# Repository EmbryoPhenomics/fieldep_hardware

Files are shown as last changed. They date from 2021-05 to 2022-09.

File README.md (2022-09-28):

# fieldep_hardware
CAD files and build guides for FieldEP hardware.

Latest version of hardware comprises a camera module and a light module.

**Camera module:**
* [RPi 4](https://thepihut.com/products/raspberry-pi-4-model-b?variant=31994565689406&currency=GBP&utm_medium=product_sync&utm_source=google&utm_content=sag_organic&utm_campaign=sag_organic&gclid=Cj0KCQjwqp-LBhDQARIsAO0a6aJ3-eRsvUKjcBT1Sl6JbVKJ5IVJRQNQ4zsPwrIjGK0_9DRzZ2UdX3kaAvDAEALw_wcB)
* [Ablelectronics Breakout Pi Zero](https://www.abelectronics.co.uk/p/68/breakout-pi-zero)
* [PiJuice Zero](https://uk.pi-supply.com/products/pijuice-zero)
* [Waveshare Sim7000E](https://www.unmannedtechshop.co.uk/product/nb-iot-emtc-edge-gprs-gnss-hat-for-raspberry-pi/)
* 3.7V [12000 mAh Lithium battery](https://uk.pi-supply.com/products/pijuice-12000mah-battery)

**Light module:**
* [Sparkfun Lumidrive](https://coolcomponents.co.uk/products/lumidrive-led-driver)
* [Lumini 2" LED ring](https://coolcomponents.co.uk/products/lumini-led-ring-2-inch-40-x-apa102-2020?_pos=3&_sid=d6814a536&_ss=r)
* 3.7V Battery as big as possible. Something like [this](https://uk.pi-supply.com/products/lithium-ion-battery-pack-3-7v-4400mah) as a minimum.

<iframe src="https://myhub.autodesk360.com/ue2c78370/shares/public/SH9285eQTcf875d3c539a6b3ce2d492fae0a?mode=embed" width="640" height="480" allowfullscreen="true" webkitallowfullscreen="true" mozallowfullscreen="true"  frameborder="0"></iframe>

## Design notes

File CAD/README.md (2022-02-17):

This folder contains STL files for FieldEP electronics supports, frame and stage. 

## Internal components

Tray_plate_3-inch_Mk3_2022-Feb-17_03-37-20PM-000_CustomizedView10696725587

|Part|Note|
|----|----|
|Front plate|Fixes to O-ring flange using 4x M3x8mm countersunk precision screws|
|Rear plate|Fixes to O-ring flange using 2x M3x8mm countersunk, and 2x M3x8mm cap head precision screws|
|Offset tray|Bolts to rear plate using 1x M3x6mm cap head precision screw. Forward end of tray supported by slots in front plate|
|Tray supports|One pair, fixed to rear end of Offset tray using 2x M3x8mm countersunk precision screws per support|
|Lens mounting brackets|Minimum of one pair required. Two pairs recommended. Specific to this [microscope lens](https://shop.pimoroni.com/products/microscope-lens-0-12-1-8x); Bolted through tray using M3x14mm precision screws, hex nuts and washers between lower lens bracket and tray as required|
|Hardware summary|
|M3 X 8mm countersunk|x10|
|M3 x 8mm cap head|x3|
|M3 x 14mm cap head|x4|
|M3 hex nut|x4|
|M3 washer|x8|

Tray_plate_3-inch_Mk3_2022-Feb-17_02-23-52PM-000_CustomizedView29439711389

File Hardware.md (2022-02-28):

# Hardware configuration

## Housing

FieldEP comprises two submersible housings - cylinders of 76.2 mm internal diameter with aluminium flanges and an acrylic front window. Electronic hardware and a microscope lens are supported within the housing by a 3D-printed structure consisting of a front plate, rear plate and a tray. A LiPo battery is held underneath the tray to provide primary power to the electronics. 

The second housing is used as an auxiliary battery chamber and LED lamp which illuminates subjects from the rear, towards the camera. Animals of interest are held between the two housings on an adjustable stage, held in place with nuts on threaded bar.
99fb7549-5d30-4ef4-b056-59008e5c76de

The modular design of the support structures inside the housing allows for ease of printing on non-specialist 3D printers, and accommodates changes to electronics and battery space requirements via minor changes to the lens supports which are bolted to the forward protrusions of the electronics tray.

To summarise the main components and their function, the Raspberry Pi takes and records inputs (sensors, cameras), and transmits to a cloud-based dashboard. Power management and timing is handled by a Pi Supply PiJuice Zero, which also takes a user input to initiate bootup. Power is supplied by a LiPo cell for powering the Pi, and a D-cell battery pack which keeps the LiPo cell charged via the PiJuice Zero, and powers the LED light.

FieldEP diagram v2 drawio(1)

## Electronic components
Stacking headers are used to connect the main components to the Raspberry Pi. Stacking moPiJuicedules are connected in the order:
|Pi HAT|
|---|
|GSM Module|
|PiJuice|
|PiZero Breakout|
|Raspberry Pi Zero W 2|

Pin headers are also broken out to allow for connection to other modules. For the operation of sensors and communications the connections are broken out to a 90-degree pin header for connection via jumper wires.

|1|2|3|4|5|6|7|8|9|10|11|12|13|14|15|16|17|18|19|20|
|---|---|---|---|---|---|---|---|---|---|---|---|---|---|---|---|---|---|---|---|
|  |TX|RX| |  |  |  |  |  |  |  |  |GPIO25|GND|  |  |  |GPIO26|GND|  |
|21|22|23|24|25|26|27|28|29|30|31|32|33|34|35|36|37|38|39|40|
|3.3V|SCL|SDA|GND|  |  |  |  |  |  |  |  |  |  |  |  |  |  |  |  |  |

## Housing parts list:
* Blue Robotics 3" housing
    - [298mm Acrylic tube](https://bluerobotics.com/store/watertight-enclosures/3-series/wte3-p-tube-12-r1/) (x2)
    - [O-ring flange](https://bluerobotics.com/store/watertight-enclosures/3-series/o-ring-flange-3-series/) (x4)
    - [Aluminium end cap - 7-hole](https://bluerobotics.com/store/watertight-enclosures/3-series/wte3-m-end-cap-7-hole-r1/)
    - [Aluminium end cap - 4-hole](https://bluerobotics.com/store/watertight-enclosures/3-series/wte3-m-end-cap-4-hole-r1/)
    - [Acrylic end cap](https://bluerobotics.com/store/watertight-enclosures/3-series/wte3-p-end-cap-r1/) (x2)
    - [Switch](https://bluerobotics.com/store/comm-control-power/switch/switch-10-5a-r1/) (x2)
    - [M10 vent & plug](https://bluerobotics.com/store/cables-connectors/penetrators/vent-asm-r1/)
    - M10 penetrator for 3mm cable
    - M10 penetrator for 4.5 mm cable
    - M3 x 16 mm screws (x 20 - included with end caps)
* M8 x 250 mm threaded bar (x4)
* Faceplate
* Rear plate
* Electronics tray
* [M3 x 10 mm cap head screws](https://www.accu.co.uk/en/cap-head-screws/3975-SSCF-M3-10-A4) (x 12)
* [M3 x 16 mm cap head screws](https://www.accu.co.uk/en/cap-head-screws/3978-SSCF-M3-16-A4) (x 4)
* [M3 x 8 mm cap head screws](https://www.accu.co.uk/en/cap-head-screws/3974-SSCF-M3-8-A4) (x 3)
* [M3 x 8 mm countersunk screws](https://www.accu.co.uk/en/countersunk-socket-head-screws/5596-SSK-M3-8-A4) (x 10)
* _[M2.5 x 10 cap head screws](https://www.accu.co.uk/en/cap-head-screws/3964-SSCF-M2-5-10-A4) (x 4)_

## Electronic components
**Camera module:**
* [Raspberry Pi Zero 2 W](https://thepihut.com/products/raspberry-pi-zero-2)
* Arducam HQ camera module
* [PiJuice Zero](https://uk.pi-supply.com/products/pijuice-zero)
* [Waveshare GSM7000e SIM module](https://www.unmannedtechshop.co.uk/product/nb-iot-emtc-edge-gprs-gnss-hat-for-raspberry-pi/)
* GSM Antenna
* SIM card
* SMA connector
* Blue Robotics TSYS01 temperature sensor
* Blue Robotics I2C bus splitter
* [3.7V 12000 mAh Lithium cell](https://uk.pi-supply.com/products/pijuice-12000mah-battery)
* [Ablelectronics Breakout PiZero](https://www.abelectronics.co.uk/p/68/breakout-pi-zero)
* Extra long stacking pin header for Raspberry Pi (15 mm pins)

**Light module:**
* [Sparkfun Lumidrive](https://coolcomponents.co.uk/products/lumidrive-led-driver)
* [Lumini 2" LED ring](https://coolcomponents.co.uk/products/lumini-led-ring-2-inch-40-x-apa102-2020?_pos=3&_sid=d6814a536&_ss=r)
* 3.7V Battery as big as possible. Something like [this](https://uk.pi-supply.com/products/lithium-ion-battery-pack-3-7v-4400mah) as a minimum.

_To be developed when time allows: Transistor-based switching of LED module to enable full power-down when not required. Suggested approach:_

## LED circuit

The LED light comprises an array of WS2812 LEDs, controlled via the Raspberry Pi and powered using an external battery. The LED circuit is switched using an N-channel MOSFET. 

|Schematic|Breadboard|
|----------|---------|
|LED MOSFET FieldEP_schem|LED MOSFET FieldEP_bb v2|

|Part|Detail|Role|Note|
|-----|-----|-----|-----|
|R1|330 &Omega; |Protect Pi GPIO from overcurrent| Calculated: _R = V/I_ where V is the power supply voltage (4.8V) and I is the max GPIO current for Pi GPIO (16 mA)|
|R2|100 k&Omega;|Pull-down resistor|Ensure Gate pin on MOSFET is stable|Recommend high value|
|Q1|[IRLB8721](https://uk.rs-online.com/web/p/mosfets/7259322)|Switches LED circuit|Logic-level N-channel MOSFET. Relies on voltage difference between Gate and Source (Pins 1 & 3). Alternatives include [IRLZ44ZPBF](https://uk.rs-online.com/web/p/mosfets/6887308) and [FQP30N06L](https://uk.rs-online.com/web/p/mosfets/8075863)|
|WS2812|RGB LED|Illumination!|May need a 1N4001 diode between battery positive terminal and VDD if unexpected behaviour occurs due to logic level discrepancy between Pi (3.3V) and LED (5V)| 
|C1|1000 &mu;F|Compensates for spikes in current draw|Recommended but not essential|

https://bluerobotics.com/store/cables-connectors/penetrators/penetrator-10-25-a/
https://bluerobotics.com/store/cables-connectors/penetrators/penetrator-blank-10-25-a-r2/

## Consumables
* Solder
* [Epoxy encapsulant] (https://uk.rs-online.com/web/p/potting-compounds/1991430/?cm_mmc=UK-PLA-DS3A-_-google-_-CSS_UK_EN_Adhesives_%26_Sealants_%26_Tapes_Whoop-_-Potting+Compounds_Whoop+(2)-_-1991430&matchtype=&pla-361646333034&gclid=Cj0KCQiA-aGCBhCwARIsAHDl5x_ZlQvM5ZzL2Q7NVCp0c83qOvFK9o2Kul7I_UrpGSP3q1dLpcyBrxwaAjktEALw_wcB&gclsrc=aw.ds)
* Wire (22 AWG)

## Switch mode operation
FieldEP is designed to boot up into one of two modes. The process of bootup up is the same regardless of which mode is required. The _Boot_ switch is momentarily partially unscrewed (3(?) full turns). This initiates a boot cycle, whereby the state of the _Mode_ switch is monitored, and the system boots into the selected mode. 

During Live View mode, a change in state of the _Mode_ switch will power the system down. 

A typical deployment procedure would be:

1) Position stage approximately where laboratory testing has shown focus point to be with chosen magnification
2) Set _Mode_ to _Live_
3) Boot system by momentarily unscrewing _Boot_ switch until system powers up
4) Close _Boot_ switch
5) Immerse system in shallow water, LED lamp module first
6) Monitor live view whilst manipulating position of stage until focus is achieved
7) Change _mode_ switch to _Deployment_ by fully screwing closed
8) Boot system by momentarily unscrewing _Boot_ switch until system powers up

Step 8 initiates an acquisition cycle. The first acquisition will occur immediately and subsequent acquisitions will occur according to the time delay set in config.json.

Operation modes - coloured background

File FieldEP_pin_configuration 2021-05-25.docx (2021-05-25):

Function | Module | GPIO | Pin # | | GPIO | Module | Function
Sensor power | I2C sensors | 3.3V | 1 | 2 | 5V
Sensor SDA | I2C sensors | GPIO2 SDA (I²C) | 3 | 4 | 5V
Sensor SCK | I2C sensors | GPIO3 SCK (I²C) | 5 | 6 | GND | I2C sensor GND | GND
| | GPIO4 | 7 | 8 | GPIO14 (UART TX) | SIM800 RX | Receive
| | GND | 9 | 10 | GPIO15 (UART RX) | SIM800 TX | Transmit
| | GPIO17 Chip Enable-CE1 (SPI1) | 11 | 12 | GPIO18 Chip Enable-CE0 (SPI1) [PWM] | LiPo Shim Pin 12 | Low-voltage shutdown signal
| | GPIO27 | 13 | 14 | GND | SIM800 GND | GND
| | GPIO22 | 15 | 16 | GPIO23
3.3V ref voltage | LiPo Shim | 3.3V | 17 | 18 | GPIO24
| | GPIO10 MOSI (SPI0) | 19 | 20 | GND
| | GPIO9 MISO (SPI0) | 21 | 22 | GPIO25
| | GPIO SCLK (SPI0) | 23 | 24 | GPIO8 Chip Enable-CE0 (SPI0)
| | GND | 25 | 26 | GPIO7 Chip Enable-CE1 (SPI0)
| | GPIO 0 EEPROM SDA (I²C) | 27 | 28 | GPIO 1 EEPROM SCK (I²C)
| | GPIO5 | 29 | 30 | GND
| | GPIO6 | 31 | 32 | GPIO12 (PWM)
| | GPIO13 (PWM) | 33 | 34 | GND
| | [PWM] GPIO19 MISO (SPI1) | 35 | 36 | GPIO16 Chip Enable-CE2 (SPI1)
| | GPIO26 | 37 | 38 | GPIO 20 MISO (SPI1)
| | GND | 39 | 40 | GPIO 21 SCLK (SPI1)

LiPo Shim Pinout

Function | GPIO | Pin # | | GPIO | Function
Provides 3.3V reference voltage to trigger safe shutdown. | 3.3V | 1 | 2 | 5V | Provides 5V to Witty Pi3 Mini power management board.
| | 3 | 4
| | 5 | 6 | GND | Ground
| | 7 | 8
| | 9 | 10
| | 11 | 12 | GPIO18 | Connects to Pi GPIO18 to provide the shutdown signal when low voltage (< 3.3V) detected on battery.

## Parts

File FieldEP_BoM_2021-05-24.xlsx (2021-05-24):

Module | Category | Item | URL | Count | Unit cost | Subtotal | Note
Camera | Controller | Raspberry Pi Zero W | https://thepihut.com/products/raspberry-pi-zero-w?variant=31901049749566&currency=GBP | 1 | £9.30 | £9.30
Camera | I/O | GPIO Breakout for Pi Zero | https://www.robotshop.com/uk/prototyping-hat-raspberry-pi-zero.html | 1 | £4.69 | £4.69
Camera | I/O | Microscope lens | https://shop.pimoroni.com/products/microscope-lens-0-12-1-8x | 1 | £22.50 | £22.50
Camera | I/O | Raspberry Pi HQ Camera | https://thepihut.com/collections/raspberry-pi-camera/products/raspberry-pi-high-quality-camera-module | 1 | £49.50 | £49.50
Camera | Comms | Waterproof cable | https://thepihut.com/products/waterproof-polarized-4-wire-cable-set?variant=27740485329&currency=GBP | 1 | £2.50 | £2.50
Camera | Comms | GSM Module (Adafruit Fona 32u4) | https://thepihut.com/products/adafruit-feather-32u4-fona | 1 | £40.00 | £40.00
Camera | Power | Power shield (Witty Mini3) | https://thepihut.com/products/witty-pi-3-mini-rtc-power-management-for-raspberry-pi-zero | 1 | £17.00 | £17.00
Camera | Power | DC-DC converter (LiPo Shim) | https://thepihut.com/products/lipo-shim | 1 | £11.40 | £11.40
Camera | Power | Battery 12000 mAh | https://uk.pi-supply.com/products/pijuice-12000mah-battery?_pos=1&_sid=39c6b1511&_ss=r | 1 | £29.99 | £29.99
Light | Power | Battery 5000 mAh | https://uk.pi-supply.com/products/pijuice-5000mah-battery?_pos=4&_sid=39c6b1511&_ss=r | 1 | £25.00 | £25.00
Camera & Light | Power | JST connector | https://thepihut.com/products/jst-ph-2-pin-cable-female-connector-100mm | 2 | £0.50 | £1.00
Camera | Comms | Antenna | https://uk.rs-online.com/web/p/gsm-gprs-antennas/1248692/ | 0 | £14.22 | £0.00
Camera | Comms | Antenna - mini | https://thepihut.com/products/slim-sticker-type-gsm-cellular-quad-band-antenna-3dbi-200mm | 1 | £2.60 | £2.60
Camera | Control | Micro SD card | https://uk.rs-online.com/web/p/micro-sd-cards/1747339/ | 1 | £32.10 | £32.10
Camera | Comms | Sim card | https://www.1pmobile.com/ | 1 | £10.00 | £10.00
Camera | Comms | Data allowance | https://www.1pmobile.com/ | 1000 | £0.01 | £10.00 | 1 Gb per card? Need to check data reqs..
Camera | Housing | Housing 3" x 298 mm | https://bluerobotics.com/store/watertight-enclosures/3-series/wte3-p-tube-12-r1/ | 1 | £86.00 | £86.00
Light | Housing | Housing 3" x 222 mm | https://bluerobotics.com/store/watertight-enclosures/3-series/wte3-p-tube-8p75-r1/ | 1 | £65.00 | £65.00
Camera & Light | Housing | Flange 3" | https://bluerobotics.com/store/watertight-enclosures/3-series/o-ring-flange-3-series/ | 4 | £24.00 | £96.00
Camera & Light | Housing | Acrylic faceplate | https://bluerobotics.com/store/watertight-enclosures/3-series/wte3-p-end-cap-r1/ | 2 | £10.00 | £20.00
Camera | Housing | Rear plate 7-hole | https://bluerobotics.com/store/watertight-enclosures/3-series/wte3-m-end-cap-7-hole-r1/ | 1 | £14.00 | £14.00
Light | Housing | Rear plate 4-hole | https://bluerobotics.com/store/watertight-enclosures/3-series/wte3-m-end-cap-4-hole-r1/ | 2 | £12.00 | £24.00
Camera & Light | Housing | Vent and plug | https://bluerobotics.com/store/cables-connectors/penetrators/vent-asm-r1/ | 2 | £9.00 | £18.00
Camera & Light | Housing | M10 Penetrator | https://bluerobotics.com/store/cables-connectors/penetrators/penetrator-10-25-a/ | 8 | £4.00 | £32.00
Camera & Light | Housing | M10 Penetrator blank | https://bluerobotics.com/store/cables-connectors/penetrators/penetrator-blank-10-25-a-r2/ | 8 | £4.00 | £32.00
Camera | Housing | Power switch penetrator | https://bluerobotics.com/store/comm-control-power/switch/switch-10-5a-r1/ | 1 | £15.00 | £15.00
Camera | Housing | Spare o-ring kit | https://bluerobotics.com/store/watertight-enclosures/3-series/wte3-o-ring-set-r1/ | 2 | £3.00 | £6.00
Camera | I/O | Temperature sensor | https://bluerobotics.com/store/sensors-sonars-cameras/sensors/celsius-sensor-r1/ | 1 | £60.00 | £60.00
Camera | I/O | Pressure sensor (high resolution 10 metre max depth) | https://bluerobotics.com/store/sensors-sonars-cameras/sensors/bar02-sensor-r1-rp/ | 1 | £88.00 | £88.00
Camera & Light | Housing | Potting compound | https://uk.rs-online.com/web/p/potting-compounds/1991430/?matchtype=&pla-361646333034&gclsrc=aw.ds | 1 | £15.00 | £15.00
Camera & Light | Frame | Jubilee clips stainless | https://www.accu.co.uk/en/worm-drive-hose-clamps/69961-HHC-90-12-20-A2 | 4 | £3.00 | £12.00
Camera & Light | Housing | M3 bolts | https://www.accu.co.uk/en/low-head-cap-screws/8869-SSCL-M3-10-A4 | 30 | £0.26 | £7.80
Camera | Housing | M2.5 bolts | https://www.accu.co.uk/en/cap-head-screws/3964-SSCF-M2-5-10-A4 | 4 | £0.25 | £1.00
Camera & Light | Frame | M5 bolts | https://www.accu.co.uk/en/socket-button-screws/8328-SSB-M5-20-A4 | 16 | £0.30 | £4.80
Camera & Light | Frame | Aluminium extrusion | https://reprapworld.co.uk/products/mechanical/frames_and_bars/frames/aluminum_extrusion_20x20mm/ | 3 | £8.10 | £24.30
Light | Controller | LumiDrive | https://coolcomponents.co.uk/products/lumidrive-led-driver | 1 | £19.99 | £19.99
Light | I/O | Lumini 2" | https://coolcomponents.co.uk/products/lumini-led-ring-2-inch-40-x-apa102-2020 | 1 | £16.00 | £16.00
Camera & Light | Misc | Miscellany | Wire & Solder | 1 | £1.00 | £1.00
Camera & Light | Misc | 3D printing consumables | Filament etc - incl potentially using MarkForge carbon fibre printing | 1 | £100.00 | £100.00
Camera & Light | Housing | Biofouling wipers | A conservative estimate | 1 | £100.00 | £100.00
Camera | I/O | pH sensors? - would be good to validate these alongside WRT's | http://www.warburtech.co.uk/products/sensors/ph/atlas.scientific.kit-101p.ph.kit/ | 0 | £124.00 | £0.00
Camera | I/O | O2 sensors - would be good to validate these alongside WRT's | http://www.warburtech.co.uk/products/sensors/dissolved.oxygen/atlas.scientific.kit-103d.dissolved.oxygen.kit/ | 0 | £220.00 | £0.00
Camera | I/O | Conductivity K1.0 kit | http://www.warburtech.co.uk/products/sensors/conductivity/atlas.scientific.ec-kit-1.0.conductivity.k.1.0.kit/ | 0 | £163.00 | £0.00
Camera | I/O | Tentacle T3 | http://www.warburtech.co.uk/products/sensors/accessories/atlas.scientific.ten-t3.whitebox.labs.tentacle.t3.for.raspberry.pi/ | 0 | £87.50 | £0.00
 |  | Total |  |  |  | £1111.48

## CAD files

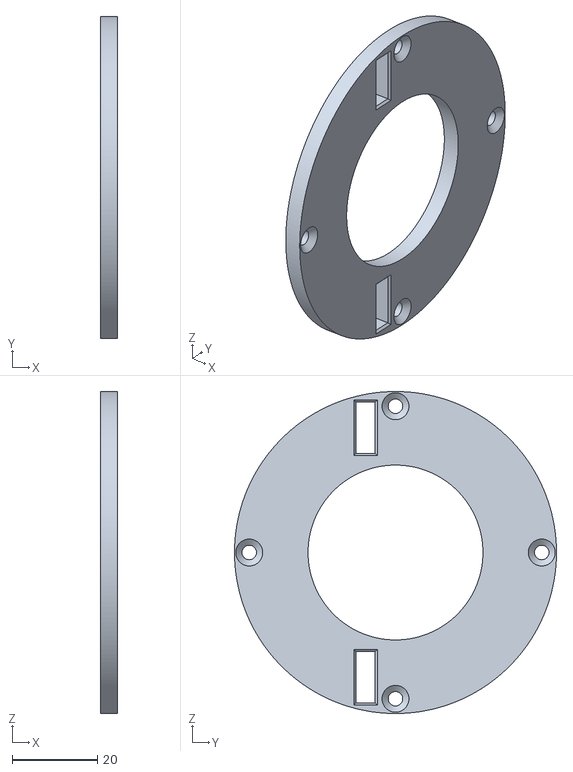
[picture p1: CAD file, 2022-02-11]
CAD/Front_disc.stl
4.00 x 75.5 x 75.5

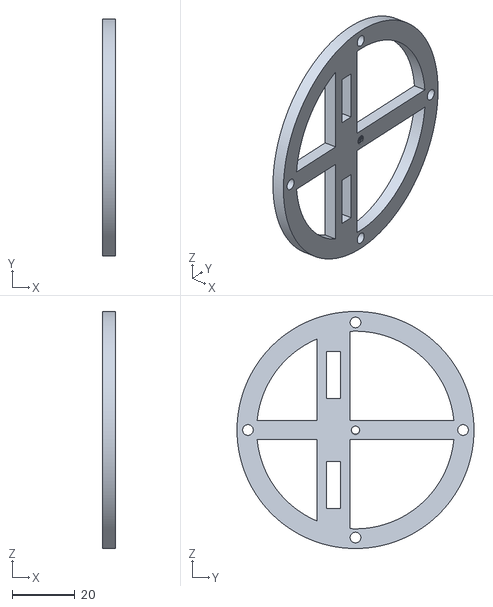
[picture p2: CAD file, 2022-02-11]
CAD/Rear_disc.stl
4.00 x 75.6 x 75.6

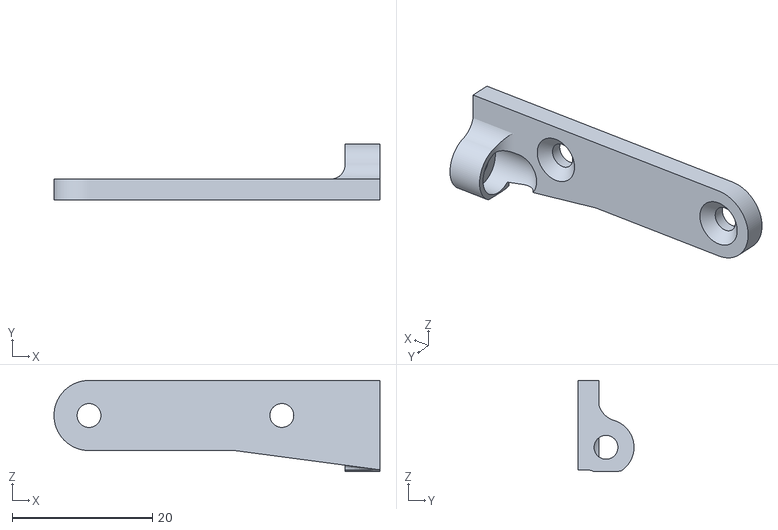
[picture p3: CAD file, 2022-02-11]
CAD/Tray supports_Tray_plate_3-inch_Mk3 v24_Body1_Tray supports.stl
46.5 x 8.00 x 13.0

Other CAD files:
CAD/Tray supports_Tray_plate_3-inch_Mk3 v24_Body4_Tray supports.stl

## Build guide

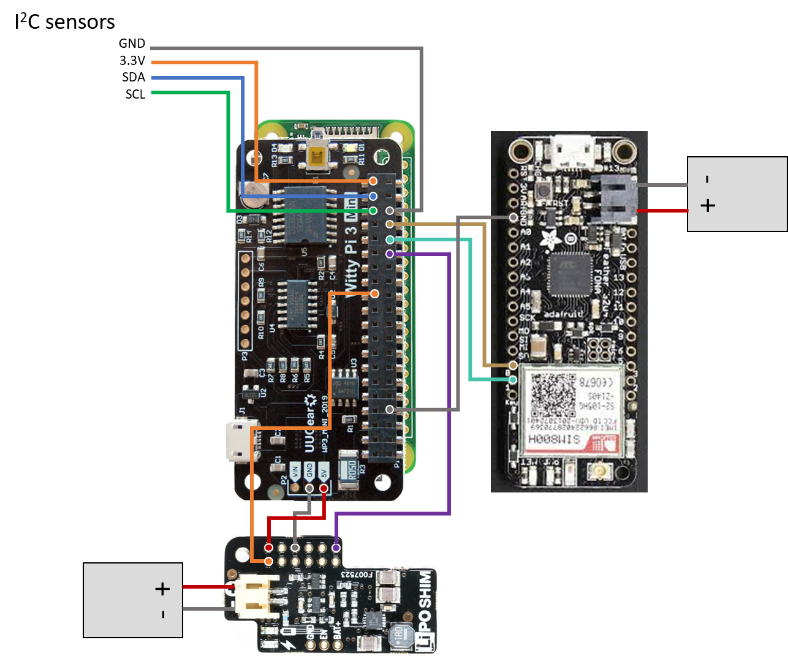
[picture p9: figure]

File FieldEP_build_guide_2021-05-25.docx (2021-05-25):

Steps taken in the development of the Field EP devices

# 1) Hardware:

Part | Role
Raspberry Pi Zero W | Main controller
LiPo Shim | Boost converter 3.7V to 5V
Witty Pi Mini3 | Power management
Adafruit Feather Fona 32u4 | GPRS network connection
Raspberry Pi HQ camera | Camera sensor
Blue Robotics TSYS01 | Temperature sensor

Pinout diagrams are provided in Appendix 1.

## 1.1. Hardware connections

The hardware of the FieldEP comprises a suite of modules which provide all required functionality. Connections are summarised in Appendix 2. The base unit is a Raspberry Pi Zero (RPi) single-board computer, which is powered from a 3.7V lithium battery, via a boost converter to increase the voltage to 5V. This power is supplied via the power management board, which controls the duty cycle of the FieldEP. The boost converter monitors battery power and signals for a safe shutdown of the Pi if it detects a voltage below 3V.

At present, the power management board does not shut down the boost converter board. This will be incorporated once duty cycles and power budgets are being optimised during field testing.

Environmental sensors use the I²C bus for data transfer, with TSYS01 occupying I²C address 77. Care should be taken to ensure other environmental sensors occupy different addresses. Environmental sensors can be connected in parallel to the same pins as the TSYS01 sensor. Be aware that some environmental sensors are sensitive to electronic interference (e.g. pH and some O2 sensors) and require voltage isolation.

Data are transmitted using a SIM800L board or an Adafruit Feather Fona 32u4 microcontroller with integrated SIM800H board. These make use of the serial UART communication to send and receive data using AT-commands.

# 2) Raspberry Pi configuration

The hardware components need to be integrated on the RPi platform. This ensures the relevant drivers are available and that the necessary GPIO pins are accessible or reassigned where necessary.

GPIO clashes

With the current hardware setup, there is a clash where the 1-wire interface is enabled on GPIO4 by default. The Witty Pi Mini3 and LiPo shim both require this pin for low-voltage safe shutdown signals.

It is therefore necessary to make the following changes:

Change 1-wire interface from GPIO4 to GPIO21.

Once LiPo Shim daemon has been installed, change the trigger GPIO from GPIO4 to GPIO18.

Install the relevant drivers and modules on the Pi.

Item | Install | Install method
Witty Pi3 Mini

Connect the hardware

Check the hardware

Run a test script

Set up the bootup file to run a script on startup

Reboot to test operation

Set up duty cycle in Witty Pi GUI

LiPo Shim | One-line install to operate safe shutdown function | https://github.com/pimoroni/clean-shutdown | Change pin from GPIO4 to GPIO18. This is the last pin available on the LiPo shim, since the others are in use for other comms.
Adafruit Feather 32u4 Fona
Witty Pi3 Mini | Install GUI | | Change 1-wire interface to a pin other than GPIO4… set to GPIO21
| Configure Pi for using UART | https://www.raspberrypi.org/documentation/configuration/uart.md
| Install TSYS01 driver from BlueRobotics Github

# Appendix 1: Pinout diagrams

## Appendix 1.1: Raspberry Pi Zero W

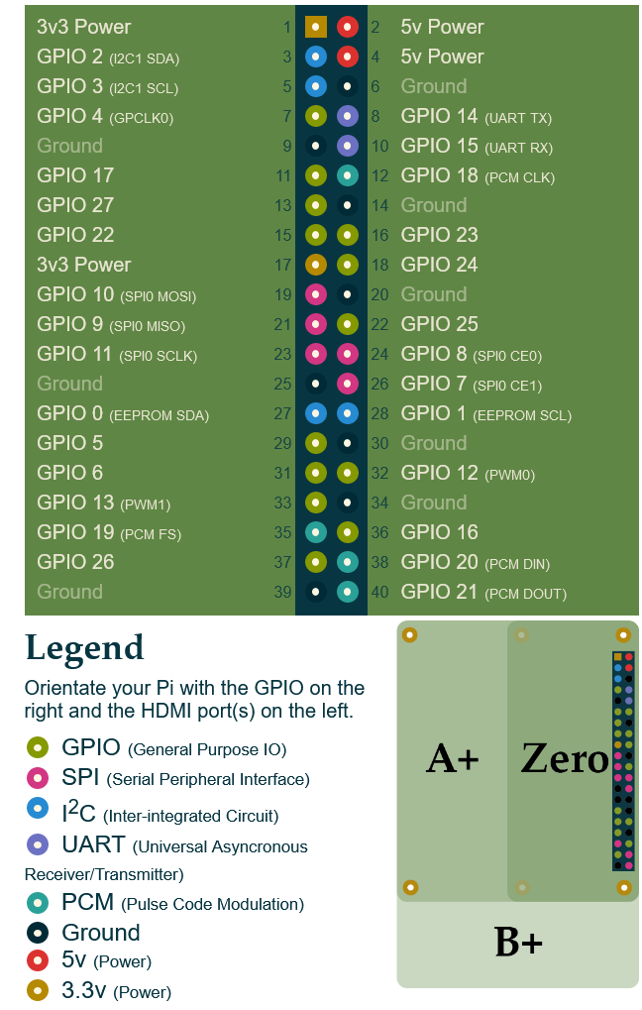
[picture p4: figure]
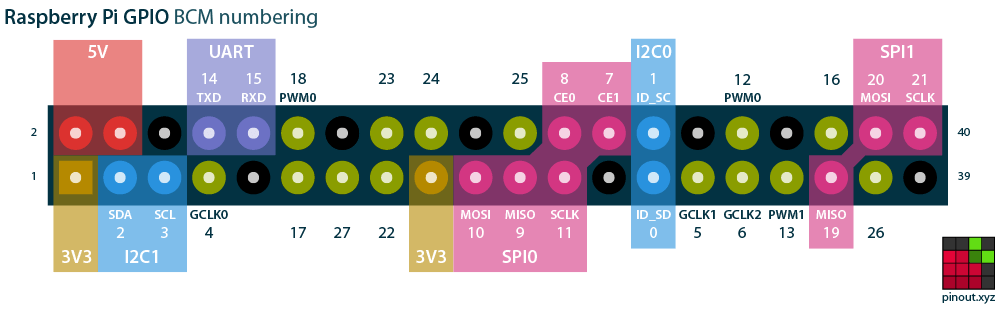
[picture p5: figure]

| https://pinout.xyz/#

## Appendix 1.2: LiPo shim

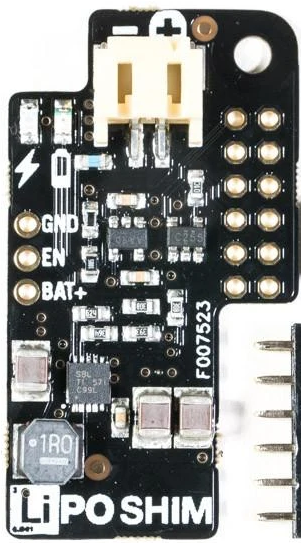
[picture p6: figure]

## Appendix 1.3: Witty Pi 3 Mini

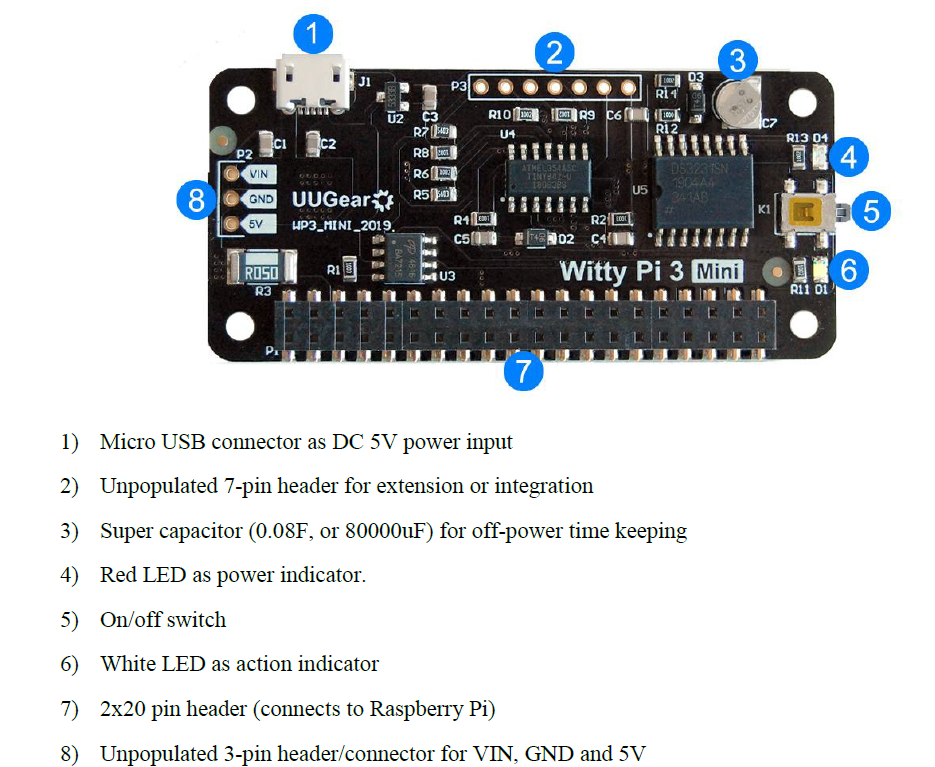
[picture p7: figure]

## Appendix 1.4: Adafruit Feather 32u4 Fona

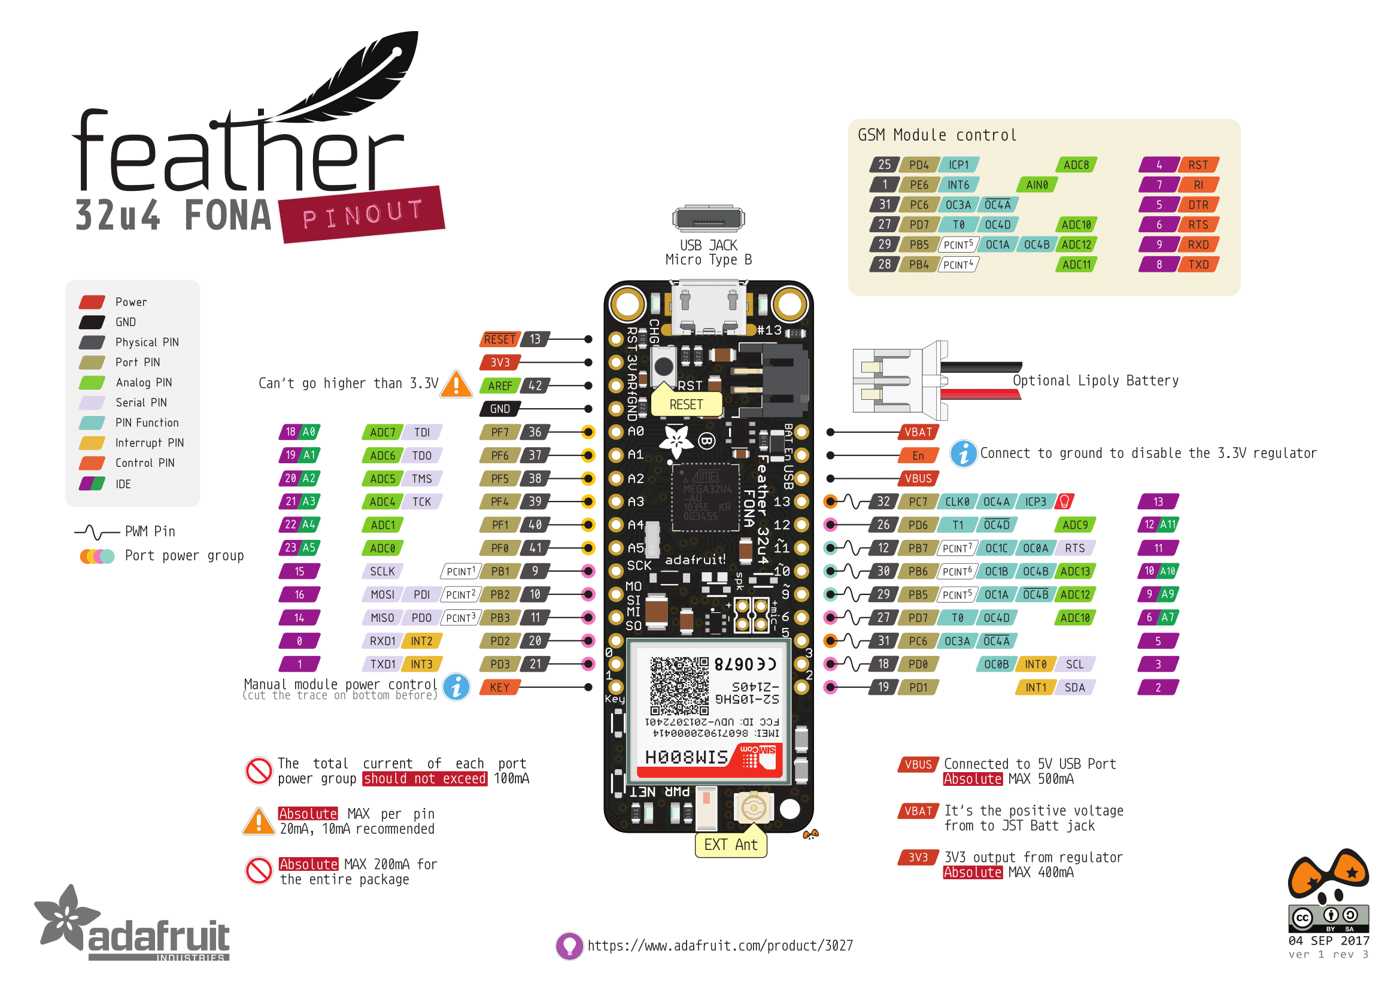
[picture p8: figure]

# Appendix 2: Summary of hardware connections to RPi.

Function | Module/Pin | GPIO | Rpi | pin | GPIO | Module/Pin | Function
Sensor power | I²C board/VCC | 3.3V | 1 | 2 | 5V
I2C serial data | I²C board/SDA | GPIO2 SDA (I²C) | 3 | 4 | 5V
I2C serial clock | I²C board/SCK | GPIO3 SCK (I²C) | 5 | 6 | GND | I2C board/GND | Ground
| | GPIO4 | 7 | 8 | GPIO14 (UART TX) | SIM800/4 | Rx
| | GND | 9 | 10 | GPIO15 (UART RX) | SIM800/5 | Tx
| | GPIO17 Chip Enable-CE1 (SPI1) | 11 | 12 | GPIO18 Chip Enable-CE0 (SPI1) [PWM] | LiPo Shim/12 | Low-voltage shutdown signal
| | GPIO27 | 13 | 14 | GND
| | GPIO22 | 15 | 16 | GPIO23
3.3V reference | LiPo Shim/1 | 3.3V | 17 | 18 | GPIO24
| | GPIO10 MOSI (SPI0) | 19 | 20 | GND
| | GPIO9 MISO (SPI0) | 21 | 22 | GPIO25
| | GPIO SCLK (SPI0) | 23 | 24 | GPIO8 Chip Enable-CE0 (SPI0)
| | GND | 25 | 26 | GPIO7 Chip Enable-CE1 (SPI0)
| | GPIO 0 EEPROM SDA (I²C) | 27 | 28 | GPIO 1 EEPROM SCK (I²C)
| | GPIO5 | 29 | 30 | GND
| | GPIO6 | 31 | 32 | GPIO12 (PWM)
| | GPIO13 (PWM) | 33 | 34 | GND
| | [PWM] GPIO19 MISO (SPI1) | 35 | 36 | GPIO16 Chip Enable-CE2 (SPI1)
| | GPIO26 | 37 | 38 | GPIO 20 MISO (SPI1)
GND | SIM800/6 | GND | 39 | 40 | GPIO 21 SCLK (SPI1)

# Appendix 3: Connection diagram.
